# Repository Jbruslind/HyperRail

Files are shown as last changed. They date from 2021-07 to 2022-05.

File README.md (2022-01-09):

<<<<<<< HEAD
# HyperRail

### temporary message- Please view these branches for latest work on HyperRail from Fall 2021 cs467 course.
Currently branches are working with mock data or demo nodes and will be merged to main when it is ideal.

-web_ui (web app development)
https://github.com/Jbruslind/HyperRail/tree/web-ui/WebUI

-ros_sensor_interpretation (self explanatory)
https://github.com/Jbruslind/HyperRail/blob/ros_sensor_interpretation/src/hyper_rail/nodes/README.md

-ros_pathplanning (self explanatory) - https://github.com/Jbruslind/HyperRail/tree/ros_pathplanning
  -merged HyperRail/src from ros_pathplanning to main

-ros_camera_latest (Micasense camera) - https://github.com/Jbruslind/HyperRail/tree/ros_camera_latest

# eGreenhouse 2.0

### Rewrite for cleaner faster eGreenhouse sensor package
=======
# ros_camera_latest Branch

Objective: 
- capture MicaSense images
- transfer image files from SD of Micasense Camera to external storage drive
- store file path of images, along with unique id's to SQLlite database for later retrieval 
- delete files from SD card of MicaSense camera once transfered to external storage drive

Camera details:

[Micasense RedEdge-MX](https://micasense.com/rededge-mx/) 

[HTTP Micasense API](https://micasense.github.io/rededge-api/api/http.html)

Note: Camera API makes request to 192.168.1.83:80 by default

By default, the ethernet IP address is 192.168.1.83 

Please follow [guide](https://support.micasense.com/hc/en-us/articles/215173477-How-do-I-connect-to-MicaSense-sensors-) to connect to camera via ethernet

### Setting up enviromental paths
>>>>>>> ros_camera_latest

The following should be added to your bash.rc or zsh equivalent
```Bash
# Goes above all other source calls
export PYTHONPATH="<Absolute Path>/HyperRail/src/hyper_rail/src"

source <Absolute Path>/HyperRail/devel/setup.bash  
```

<<<<<<< HEAD
If there is a better way to do this please tell me cause this is really annoying

### Basic File Structure Information
---
- src
    - ROS programs, contains all nodes, message types, scripts, and source files. Some ROS functionality is dependent on having the database set up and seeded.
- WebUI
    - Web interface, database, image storage
- ImageProcessing
    - Code created during image stitching research, includes script for generating test images that can be used with the compositor. Compositor depends on having database setup
- stable_firmware
    - stable version and firmware of GRBL to control the appropriate driving hardware

&nbsp;

# ROS Programs
## Description
The HyperRail is controlled by the following nodes and communicate through the message types listed below.
* ProgramNode - Recevies program_ids over `ProgramFeed` topic, gets list of waypoints for the program from the database, coordinates sending movement instructions, data collection instructions, and initiating image stitching.
* MotionNode - Receives individual waypoints from ProgramNode over `MotionService` service, generates GCodes to send to the ESP32 controller. Publishes GCodes to `GCodeFeed` Topic

The following nodes were used during development to test the topics and services. They are available for demonstration, but not used once running with the final hardware.
* ESPMock - Receives over `GCodeFeed`, publishes location to `MachinePosition`
* CameraMock - Receives requests and sends responses through `SensorService`
* SensorMock - Receives requests and sends responses through `SensorService` 

ROS nodes make use of executor classes, db queries, image processing, and constants stored in `~/HyperRail/src/hyper_rail/src`

# Running the ROS programs
In addition to ROS The following libaraies should be installed, either to a virtual environment or globally
* `pip install opencv-python`
* `pip install imutils`
* `pip install argparse`
* `pip install numpy`
* `pip install wheel`
* `pip install pgmagick`

A `Requirements.txt` is included in `~/HyperRail/src` and can be installed with pip

Related topics and services used by the nodes are located in `../srv` and `../msg`

Class definitions used in ProgramNode and MotionNode are located in `../src/communication`

To run the provided nodes, frist run `catkin_make` in the root directory.

The included nodes can be run with the given launch file using one of the following commands:
* `roslaunch hyper_rail hyper_rail_test.launch` - uses mocks for testing message passing.
* `roslaunch hyper_rail hyper_rail_launch.launch` - uses controller nodes to interact with hardware.

Including the argument `--screen` after the launch file name will print the node output to the terminal.

To run the provided nodes and mocks individually for development, run the following in separate terminals:
* `roscore`
* `rosrun hyper_rail ProgramNode`
* `rosrun hyper_rail MotionNode`
* `rosrun hyper_rail ESPMock`
* `rosrun hyper_rail CameraMock`
* `rosrun hyper_rail SensorMock`
* `roslaunch rosbridge_server rosbridge_websocket.launch`

Then send the test program id with `rostopic pub /programs hyper_rail/ProgramFeed "program_id: 1"`

# Image Processing
### File paths
Currently it is assumed that images are stored in the public directory of the web-ui `~/HyperRail/WebUI/public/images`.
Images are stored in using the file structure: `/images/{program_run_id}/{image_type}/{image file}`

Composite images are stored using the file structure: `/images/{program_run_id}/{image_type}_composite{program_run_id}.tif` 

```
public/images/
└── 1
    ├── band_1 
    │   ├── 1.tif
    │   ├── 2.tif
    │   ├── 3.tif
    └── band_1_composite1.tif
```
The image path is set in the settings page of the web-ui and stored in the settings table of the database

### Testing with temporary data
 - Note: the database must be migrated and seeded according to the database setup instrutions for database queries to work.

A test image generation script is included as `/HyperRail/ImageProcessing/drawing.py` This script generates test images which can be used for verifying the compositor crop and layout. To test with this data, generate at least one set of test images in the `~/HyperRail/WebUI/public/images` and run the `create_test_images()` database query, located in `~/HyperRail/src/hyper_rail/src/db_queries.py`. This will assign the set of test images to the waypoint runs for program run 1. 

### Execution
Then the compositor itself can be run on its own using `python compositor.py -p {program_run_id}` or through the program node. In both cases, ensure that `program_run_id` is set to 1 if using these demo instructions.

Until the camera is incorporated into the system, the `ProgramNode` calls compositor.py with a test `program_run_id` which has image paths associated to it. This is assigned at line 119 in program_executor.py and should be removed when the camera is added.

## ToDo:
- Create robust error handling for lost connection with hardware components
- Test with hardware
- Finish sensorAction() function to work with other sensor types.
=======
## Branch Highlights and Setup

### Setup Database and requirements.txt

Install [requirements.txt](https://github.com/Jbruslind/HyperRail/blob/ros_camera_latest/src/requirements.txt) in python enviroment or globally.

In order to test the Micasense Camera, a database is required

Please follow README [here](https://github.com/Jbruslind/HyperRail/tree/ros_camera_latest/WebUI).

Note: make sure schema for database is migrated over

### Test the Micasense Camera with ROS nodes.

Please follow README located [here](https://github.com/Jbruslind/HyperRail/tree/ros_camera_latest/src/hyper_rail/nodes).

Note: CameraMock node is a ros node that controls the camera and it is called via a ros-service named 'camera_service'.

CameraMock is located [here](https://github.com/Jbruslind/HyperRail/blob/ros_camera_latest/src/hyper_rail/nodes/CameraMock). 

### Test MicaSense Camera without ROS nodes.

camera_executor.py can be run [here](https://github.com/Jbruslind/HyperRail/blob/ros_camera_latest/src/hyper_rail/src/communication/camera_executor.py).

Note: the explanation for testing the Micasense Camera will be located at bottom of file below classes.

### Basic File Structure Information
---
- src
    - ROS programs, contains all nodes, message types, scripts, and source files. Some ROS functionality is dependent on having the database set up and seeded.
- WebUI
    - Web interface, database, image storage
- ImageProcessing
    - Code created during image stitching research, includes script for generating test images that can be used with the compositor. Compositor depends on having database setup
- stable_firmware
    - stable version and firmware of GRBL to control the appropriate driving hardware

### Future Plans
Needs to be tested with MicaSense camera connected via ethernet. 

Currently tested with fake data not utilizing Micasense API. 
>>>>>>> ros_camera_latest

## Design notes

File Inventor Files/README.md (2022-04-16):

---
layout: page
title: Mechanical
---

## Overview 

The Mechanical system was designed with modularity and easy assembly in mind. In the future, the system may be deployed in different areas/environment and may require an increase or decrease in dimensions.  In addition, the system will be used by users with little to no prior knowledge of how it was designed or any institutional knowledge of how it was originally assembled. With these aspects in mind, the mechanical system was created with defined "sub-assemblies" in mind so that each sub-assembly is easy to understand and assemble and can integrated into the full system seamlessly. This also allows for the option to upgrade specific sub-assemblies as needed if new ideas or designs are discovered (so long as the base needs are met). 

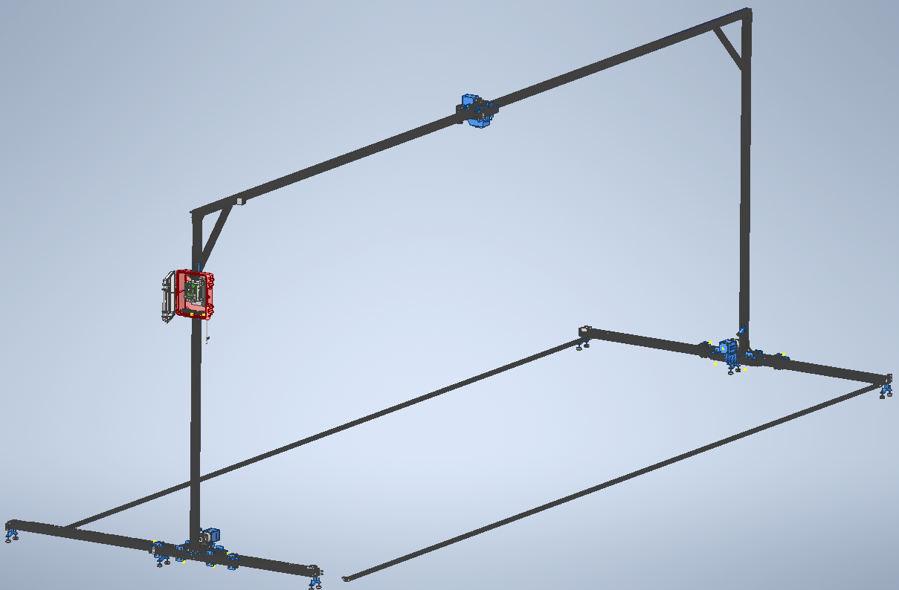
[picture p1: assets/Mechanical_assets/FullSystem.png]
Full System

### Design Objectives 
The main design objectives for this system were: 
1. Modular Sub-Assembly Structure
    * Drop-In Replacements 
    * Iteration 
    * Dynamic Length / Width 
2. Reliable Linear Motion 
    * Long Distance Motion 
    * Self-Contained 
3. Standard Materials
    * Corrosion Resistant 
    * Widely Available 
4. Standard Fasteners
    * Only 1 Allen Key Required for Assembly 
5. Limited Customized Parts
    * Minimize User Manufacturing
## X Carriage Subassembly

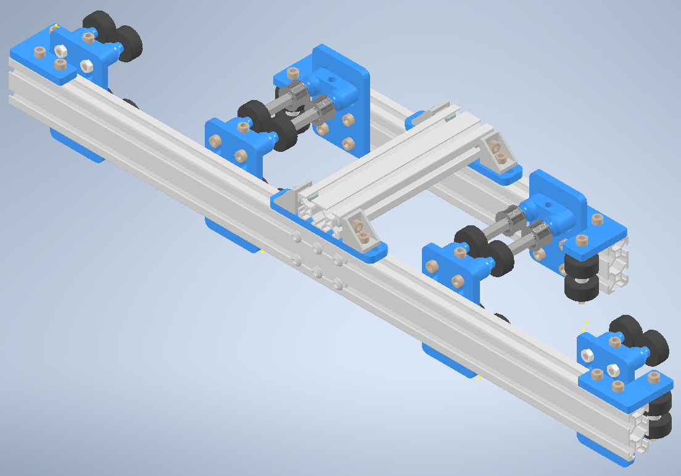
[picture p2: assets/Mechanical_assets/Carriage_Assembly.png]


The X Carriage Subassembly is the main motion platform for the HyperRail system. The assembly should allow for smooth motion along the lower 4060 T-slot track while also allowing the motor mechanism to interface to the belt track. 

The carriage assembly borrows ideas from the [Bell-Everman](https://www.bell-everman.com/products/linear-positioning/servobelt-linear-sbl)[^1] servo setup in which a static belt is used on the tracks and interfaces to a dynamic belt driven by a motor / pulley. A rack and pinion system would also work the same way (with more durability) however the realative costs were prohibitive for a system on this scale. For reference, the average cost per meter for the rack on a rack and pinion is ~$70/m whereas for this style, the belts are only ~$15/m. The projected user needs are for the system to extend up to 90ft or 30m making the rack and pinion very expensive. 

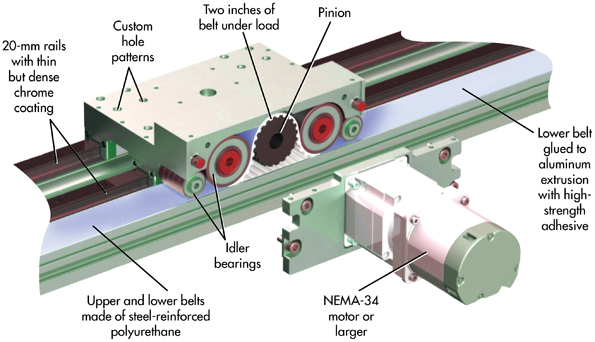
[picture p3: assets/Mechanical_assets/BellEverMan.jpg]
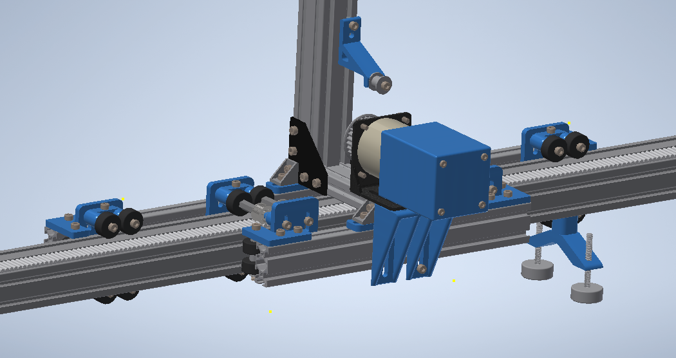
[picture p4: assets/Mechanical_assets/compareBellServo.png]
  

One of the big advantages to this style of mechanism is the ability to easily extend the track length to various sizes without needing to purchase specially made belts/tracks. This allows the overall system to maintain "modularity" with the x-direction, which is aimed to be the longer of the axes (x length >> y, z). If the user wants to add more length, they can easily attach another section of track (4060 with static belt attachment) to the original axis and align the track pieces together so the dynamic belt is able to mesh smoothly (see the Add-On module section). 

The Carriage itself is composed of 3 pieces of 2040 aluninum T slot extrusion which make up the main structural body or chassis. A long piece is used on the side with the vertical beam to give it added support and a smaller piece is used on the side with the motor. 

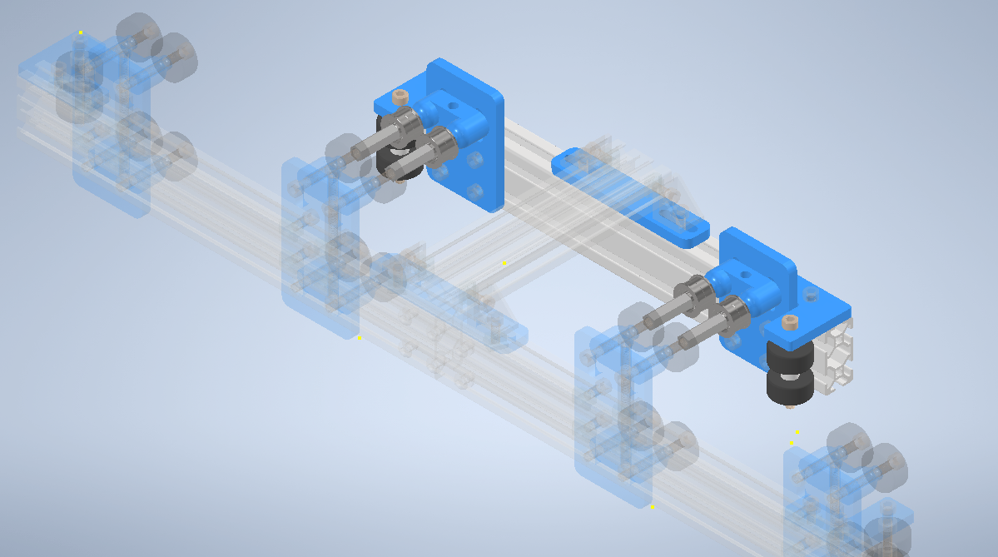
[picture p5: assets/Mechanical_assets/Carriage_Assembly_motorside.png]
Smaller Side


Individual plates with delrin wheels are used for rotational motion and structural stability. 

## X Rail Assembly

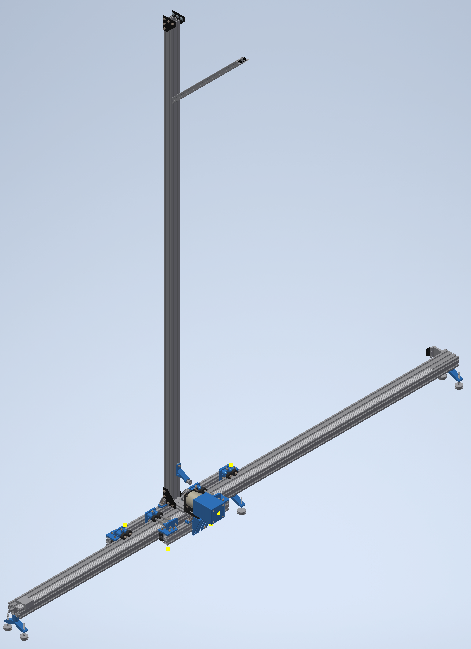
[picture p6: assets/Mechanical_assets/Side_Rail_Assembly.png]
X Rail
 Side Profile X Rail

The X Rail Assembly utilizes the carriage shown above combined with a track and vertical 4040 T-slot beam. The track itself is made of 4060 aluminum which was chosen for symmetry and stability (increased mass provides a good counterweight). In order for the mechanism to be stable, the carriage base needs to equally distribute mass where the most mass comes from the vertical beam + upper axis and the motor + planetary gearbox. Therefore the X Rail Assembly cantilevers the 2 largest masses against each other so the center of gravity is relatively centered within the X carriage.

The assembly is supported by a foot subassembly which can be added and distributed as necessary to support the system in different environments. 

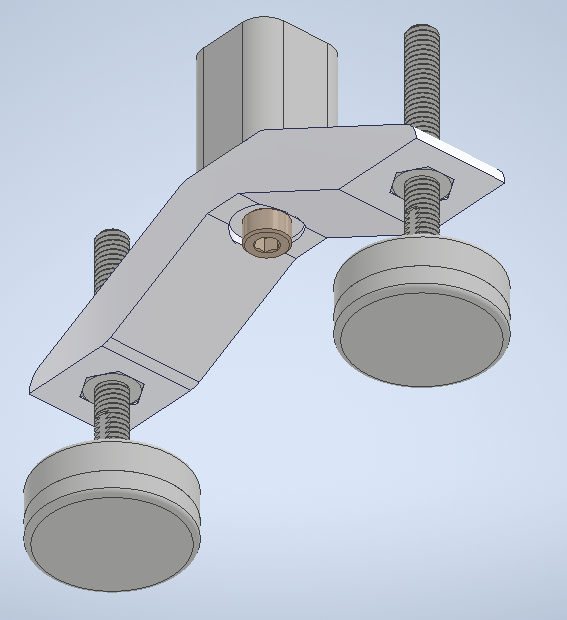
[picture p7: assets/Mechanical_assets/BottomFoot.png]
Bottom Foot


These feet allow for small height adjustments on either side through an M6 bolt embedded in the design which can be useful for outdoor use on rocky / dirt environments.

The pulley attached to the motor can be adjusted using the right angle brackets and can be used to provide tension to the belt system (height adjustment shown below). The whole mechanism can then be moved using the dynamic belt rolling along the static belt 
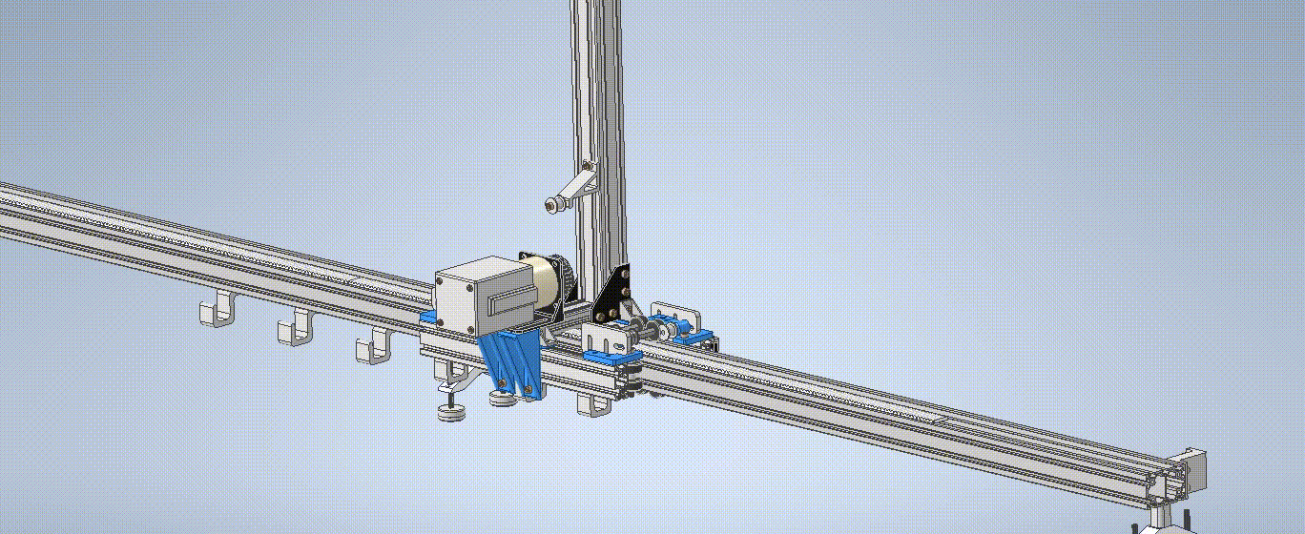
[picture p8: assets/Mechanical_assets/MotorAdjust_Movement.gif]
X Rail Movement


The static belt layer is comprised of HTD 5mm, 25mm width polyurethane belt with steel cord reinforcement from [PolyBelt](https://shop.polybelt.com/20-5M-Open-End-Belt-Roll-Polyurethane-with-Steel-Cords-B20-5M-MPS.htm). Polyurethane was chosen for its durability and resistances to outdoor environments and steel cord was chosen for its price point. Kevlar reinforcement was another option which had a better tensile modulus (lower stretching over time) however this was determined to not be a huge factor since the static belt wouldn't have large segments stretching at the same time (the stress is localized to each individual point). At the same time, Kevlar has larger thermal fluctuations [^2] which could cause problems during outdoor use in freezing / hot temperatures.

This profile is standard across many suppliers but PolyBelt was chosen for their price point and US location. In addition they had a matching closed belt profile which was the right size (6mm) and length (635mm) for the dynamic belt system.

## Top Frame Subassembly

The top frame subassembly was meant to serve as the Y-axis for the overall system and is comprised of a main 4040 T-slot extrusion paired with the same Bell-Everman style linear motion as the X-Carriages. 

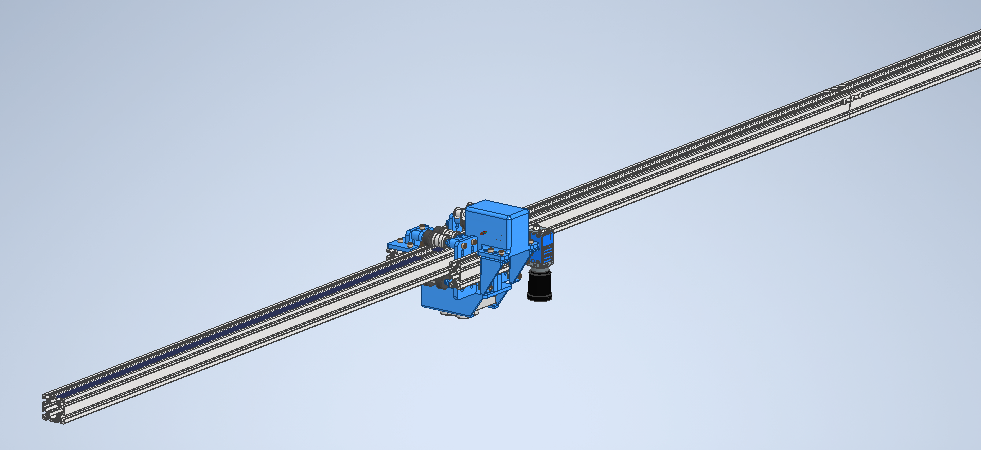
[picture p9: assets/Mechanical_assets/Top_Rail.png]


The hollow channel within the T-slot extrusion serves as a pathway for wiring from one side of the system to the other, specifically for the motor and magnetic endstop wiring. These wires are static with respect to the gantry and so can be threaded through without any torsion later. 

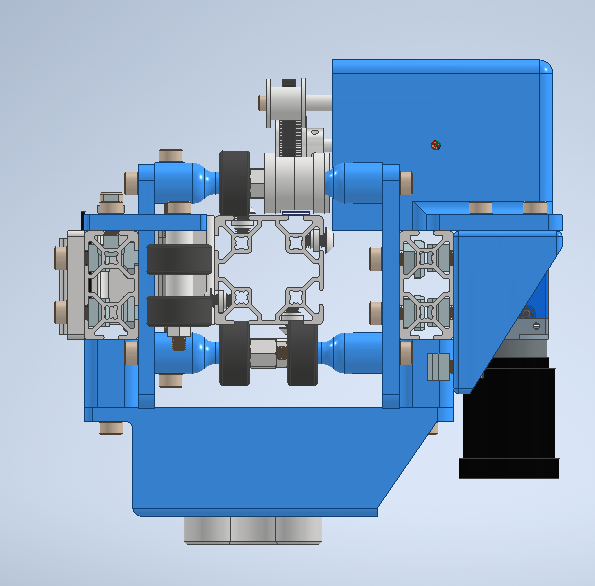
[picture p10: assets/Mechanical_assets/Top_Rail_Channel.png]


## Y Carriage Subassembly

## Ebox Subassembly

## Main System

## References
[^1]: Bell-Everman, Inc. (2016, October 19). New ServoBelt™ LoopTrack Linear Stage. Retrieved from https://www.bell-everman.com/products/linear-positioning/servobelt-linear-sbl
[^2]: When to consider Kevlar reinforced belts for linear motion applications. (2019, July 05). Retrieved from https://www.linearmotiontips.com/when-to-consider-kevlar-reinforced-belts-for-linear-motion-applications

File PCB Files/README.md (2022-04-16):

---
layout: page
title: Electrical
---

## Overview 
The electrical subsystem was designed with 3 key elements in mind: 

* Plug and Play operation 
* System Reliability 
* Expandable operation 

Plug-and-Play operation was taken to mean minimal requirements for hookups and other connections and to prioritize standard connectors that are easily available from commercial outlets. System Reliability was necessary for operation under a wide variety of conditions (wide Vin range, built-in protections, and temperature/humidity resistance) and to limit repairs by the user. Finally, it was assumed that this system should be able to accommodate other configurations than just a 3D CNC gantry and should have features that can be expanded for later development. 

## System Diagram 

System Diagram

A system diagram was created to help design the infrastructure and architecture for the overall system. In this case my idea was to approach every operable component as a "node" which could act as an independent unit. The reasoning being that I could assign each "node" to team members and give them a black box explanation for each. As an example, the motor node circuit needed to operate using the following parameters: 

+----------------------+-----------------------------------+
| Parameter            | Valid ranges                      |
+======================+===================================+
| Vin Range            | 12 - 30V                          |
+----------------------+-----------------------------------+
| Motor Current (rms)  |  2A                               |
+----------------------+-----------------------------------+
| Signal Inputs        | Step, En, Dir (STEP/DIR control)  |
+----------------------+-----------------------------------+
| Step Frequency       | < = 5Khz                          |
+----------------------+-----------------------------------+
| Microstepping        | 1x - 16x                          |
+----------------------+-----------------------------------+
| Input Interface      | RJ45 8 pin                        |
+----------------------+-----------------------------------+

By providing the specification and known inputs / outputs I could keep each node organized and have the ability to assign its development to any members that were working under my at the time. 

The main blocks in the system diagram that needed to be developed were: 
* Integrated Stepper Driver (Motor Node) 
    * Motor controller using DIR/STEP controls (or eventually UART)
* ESP32 GRBL Controller 
    * This node was meant to be the main firmware controller which would determine the signals to be sent to each motor to tell it where to move. This could be abstracted to basically just run any CNC control firmware such as Marlin, GRBL, or LinuxCNC. While researching it was determined that the ESP32 GRBL firmware met all the requirements and more with little to no development necessary (see the ESP32 GRBL section)

## Motor Nodes

Motor Node

The Motor Node PCB was meant to be an independent solution for stepper motor control. The idea was there could be many motor "nodes" which could be controlled using a known standard protocol. The controlling board could be adaptable to a variety of stepper motor types and would be easily mounted to the motor itself. 

Motor node mounted

The node has 3 I/O connectors for different purposes. The RJ45 connector (commonly used as an Ethernet connector) is used for Power and Control to the Stepper Driver IC: 

Ethernet Highlight

The pinout diagram can be found on the schematic pdfs which are included within the documentation under "HyperRail\PCB Files\Integrated Stepper Motor Driver-(fab,pcba)\PCBA-Integrated Stepper Motor Driver"

### Stepper IC 

Pinout Schematic

* Red (bottom right) | RJ-45 Pinout   
    * This Pinout is used for Power input and control signals to the TMC2209 driver IC 
* Pink (Top) | Sense Resistors 
    * The sense resistor selection is incredibly important to the TMC driver current limits. If a larger / smaller motor is required, then these should be changed to reflect that using the recommended lookup table (taken from TMC2209 Datasheet, section 8): 
    
* Yellow | VRef Selection 
    * The VRef circuit uses a simple voltage divider to maintain "soft" current limits. The idea is that the sense resistors set the "hard" current limits in that they are hardware defined whereas the voltage divider circuit allows the user to customize "soft" limits. A radial potentiometer is used for adjustable resistance and a silkscreen diagram is provided to indicate the direction to turn to increase motor current. 
* Blue | Motor Phase Outputs 
    * The output for the motor phase currents from the Stepper Driver IC is a simple 4 pin screw terminal. This allows users to use a variety of stepper motors without having to find / assemble special connectors. All that's necessary is to determine the phase diagram, strip the wires and plug in. 
    


### Power Conversion and Status LEDs



* Red | Buck Converter 
    * Main buck operating circuit which are simply an input and output capacitor and the integrated module. 
* Blue | Reverse-Protection Diode 
    * Prevents negative spikes or reverse current 

Power Conversion is done using an integrated buck controller / switch, the TI  [LMZM23601V5SILR](https://www.ti.com/product/LMZM23601). This is a wide Vin range (4 -> 36V) buck converter which will step down the power input (expected 12 - 24V) to logic level (5V) for the Stepper Driver. Not much current is expected for this application, the estimated current draw by the driver for logic level is 10mA max: 





There are 2 physical test points which were designed for multimeter probes to easily measure the voltage output during manufacture and testing. 
## ESP-32 Controller

The ESP-32 Controller was designed to be the liaison between motion requests by the ROS software and the rest of the machine. The board itself is computationally powered with an ESP32-WROOM module (either through a daughter dev-board or embedded on the board) running the [GRBL_ESP32](https://github.com/bdring/Grbl_Esp32) firmware. A key aspect of using the GRBL style firmware over other flavors (such as Marlin or otherwise) is that GRBL supports the ESP32 with no perquisites and can support a Web-UI natively for manual control. 

GRBL Controller

## Magnetic End Stops

## Main System

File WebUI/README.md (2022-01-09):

# HyperRail Web Interface

## Ruby Version

This project is a [Ruby on Rails](https://rubyonrails.org) application configured to use [Ruby](https://ruby-doc.org) version 2.7.4, but that is not a hard requirement.
Changing ruby versions will require a new Gemfile and modification to `.ruby-version`.

## Configuration

Once version 2.7.4 is installed, the rest of the gems can be installed using `bundle install`.

## Database Setup

The [SQLite](https://www.sqlite.org/index.html) database can be initialized using `bundle exec rake db:create`.
The database can be initialized using `bundle exec rake db:migrate`.
Some test data can be populated in the database by typing `bundle exec rake db:seed`.
At any point, the database can be recreated and repopulated with seed data by typing `bundle exec rake db:reset`.

The default password is `default-password` but it can be changed by creating a `Setting` in the console, or by changing the password in the `Settings` tab.
To access the console, first type `bin/rails c` and then update a `Setting` using the following example:

```ruby
# Find the existing setting or create a new one if it has not yet been created
setting = Setting.find_or_initialize_by(name: 'password')
setting.value = 'new-password-here'
setting.save!
```

## Running

To run the web server, type `bin/rails s`. By default it will run on port 3000 and can be reached at http://localhost:3000/.
Sessions are handled by storing an encrypted, signed key with the last password used and login time, and do not currently time out.
If the password setting changes, a re-login will be required as it is checked on every request.

## Default Program

Though multiple programs can be saved and run, the analysis interface assumes that there is currently a single program running that will cover the entire greenhouse. If the greenhouse settings change in terms of camera height, field of view, length, or width, a new default program will need to be generated. To do so, start the console using `bin/rails c` and run the following command (changing the name if desired):

```ruby
Program.create_from_settings(name: 'Default Program')
```

Once this has been done, you can delete the old program using the web interface.

## Default Program Generation

The default program is generated by covering the calculated greenhouse area with waypoints in a grid pattern, and then covering them using back-and-forth paths.
The grid size is calculated by using the height of the camera, its field of view, and incorporating an amount of image cropping to account for parallax due to subject proximity.
This is currently ballparked at 25% but will require experimentation with the real camera and plants in order to know if this is correct.
It is expected that this program generation will require some slight modifications once it is applied to the real hardware.

## Mock Seed Data

The `bundle exec rake db:seed` command executed above will fill in some fake sensor readings and anslyses.
A good way to get started with a new installation is to configure the default settings in `db/seeds.rb` to match the physical greenhouse and camera, and have that backfill some mock data.

## To Do

* Integrate [`rosbridge`](http://wiki.ros.org/rosbridge_suite) into a startup script so that it starts with the Rails application
* Export images once they are taken and stitched with camera ros nodes
* Add default program generation to the UI to remove a console interaction
* Map an analysis to a specific program in case the dimensions change to prevent loss of historical data
* Integrate GCode sending from relevant rosnode branch on dashboard
* Add ability to launch program manually from `Program` tab
* Dynamically scale SVG element to container panel
* Account for non-square camera images during program generation

## Development Notes:

Below are some helpful links to consider when modifying the interactive grid.

SVG Basics - https://developer.mozilla.org/en-US/docs/Web/SVG

How to properly scale svg elements - https://stackoverflow.com/questions/19484707/how-can-i-make-an-svg-scale-with-its-parent-container

SVG viewport and viewbox concepts - https://webdesign.tutsplus.com/tutorials/svg-viewport-and-viewbox-for-beginners--cms-30844

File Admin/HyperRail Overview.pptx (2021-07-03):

## hYPERrAIL pROJECT Overview

Jorian Bruslind

## Little bit about me

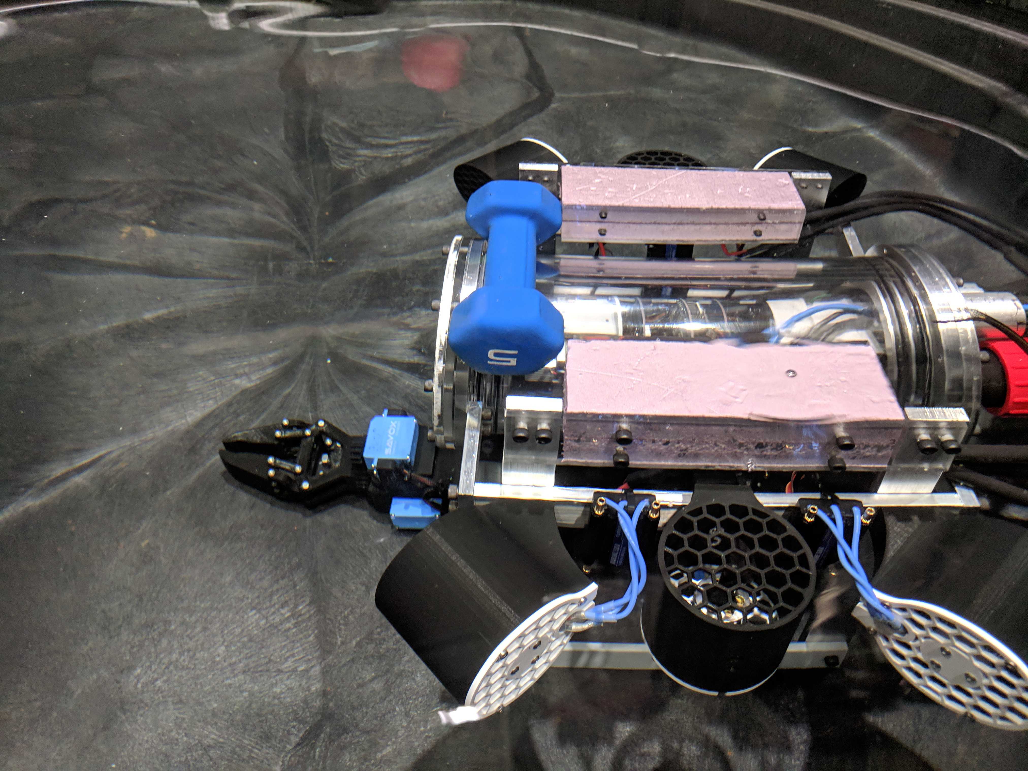
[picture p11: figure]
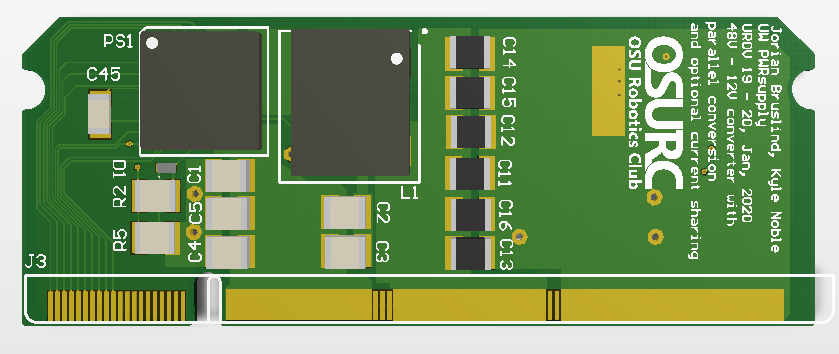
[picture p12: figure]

- Senior in ECE (Graduating at the end of Winter)
- Part of the OSU Robotics Club (2016 – 2020)
  - President (2017-2019)
  - Underwater ROV Team lead (2016-2020)
- Enjoy doing electronic projects in my spare time
  - Home automation
  - Server management / IOT networks
- Capstone Project focused on Robotics / Automated systems
  - Automated Microbial Analysis

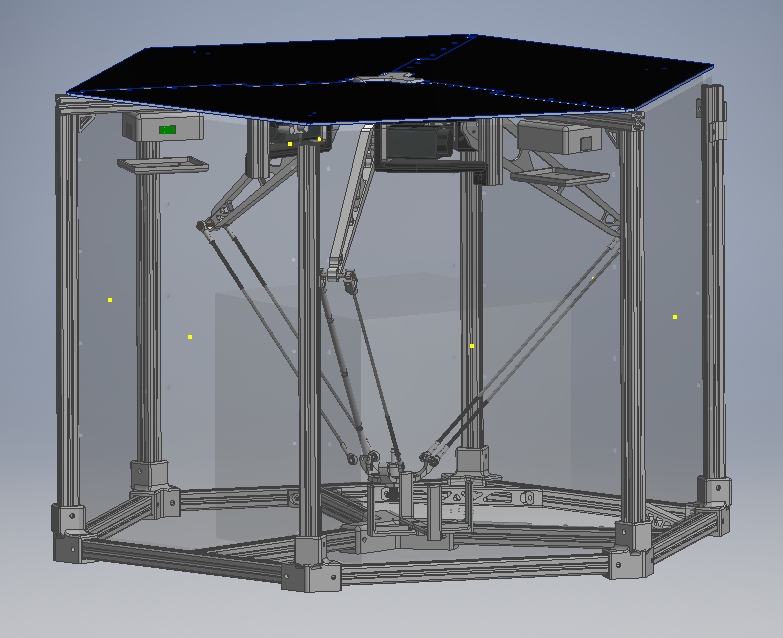
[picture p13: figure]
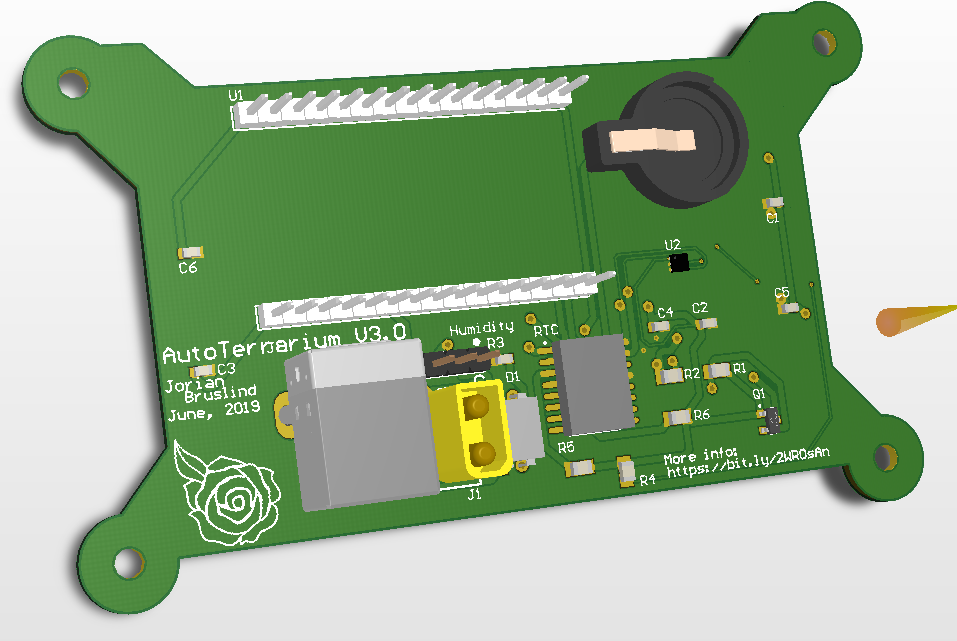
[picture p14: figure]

## Master’s program

- 45 Credit program, Project based
- Faculty advisors will serve to grade project scope and assist in planning
- Current timeline:
  - Spring 2021: 2 Project Credits (ECE 506)
  - Fall 2021: 2 Project Credits
  - Winter 2022: 4 Project Credits
  - Spring 2022: 4 Project Credits

## Current State

- Gantry like system to move an end effector in 3D space
- Axes are pretty locked up and the carriage needs some fine tuning
- Custom firmware built for stepper motor control
- Processing GUI used in conjunction with Adafruit M0 Feather
- Some LoRa capabilities

## Junior Design Groups

- 4 dedicated groups to working on the HyperRail System
- Each group is responsible for motion control using the current system (4x stepper motors + microcontroller)
- Each group has been tasked with a unique requirement to improve on the system
  - Joystick control from computer
  - Power feedback with low power algorithm
  - Path planning from image
  - Wifi control through web interface

## My work so far

- Created new 3D model using Inventor
  - Rebuilt frame and linear motion carriages using current components (with some new 3D printed components)
- Researched implementations of gantry system in similar use-cases (also some parallel cable robots)
- Created discord server for Junior Design groups and am currently helping them figure out implementations / debug
- Working with STEMbassadors for support in manufacturing / design

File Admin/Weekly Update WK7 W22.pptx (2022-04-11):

## Weekly Update

Jorian Bruslind
Week 7

## HyperRail Project

- Current Status
  - Integrated new RGB camera into system
    - Some challenges with lighting and streaming
    - Easy to use with correct software installed
  - Updated Web interface to give access to images
    - Can download latest runs as .zip files
    - Having trouble with preview function (no idea how ruby works)
  - Scheduling conflicts with defense meeting

## Current Status

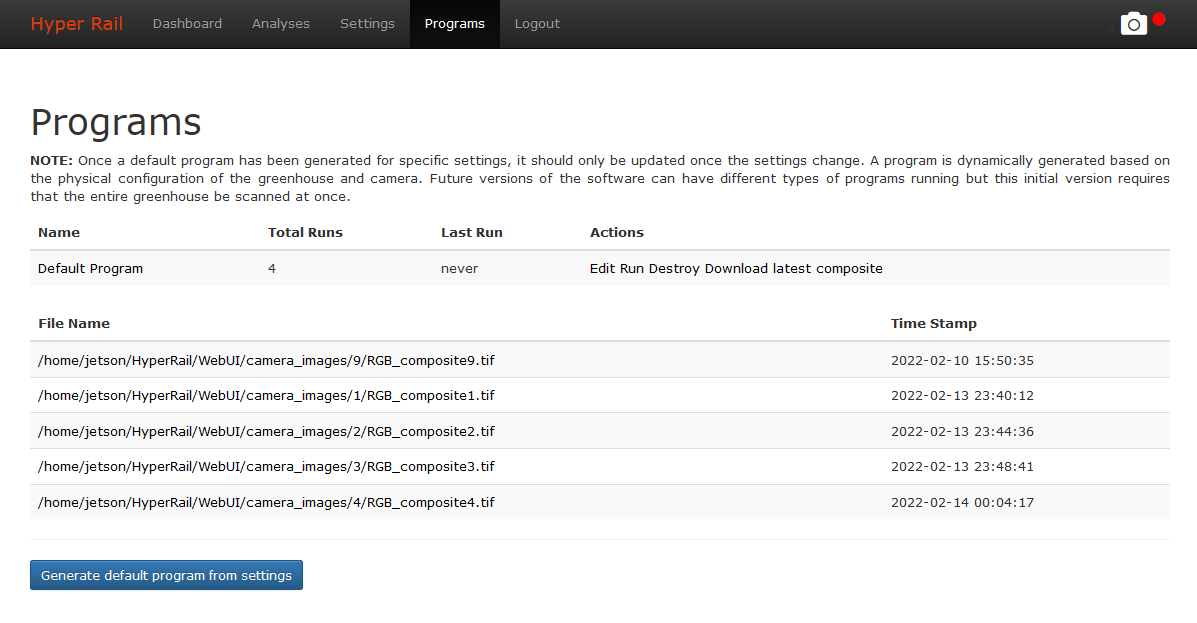
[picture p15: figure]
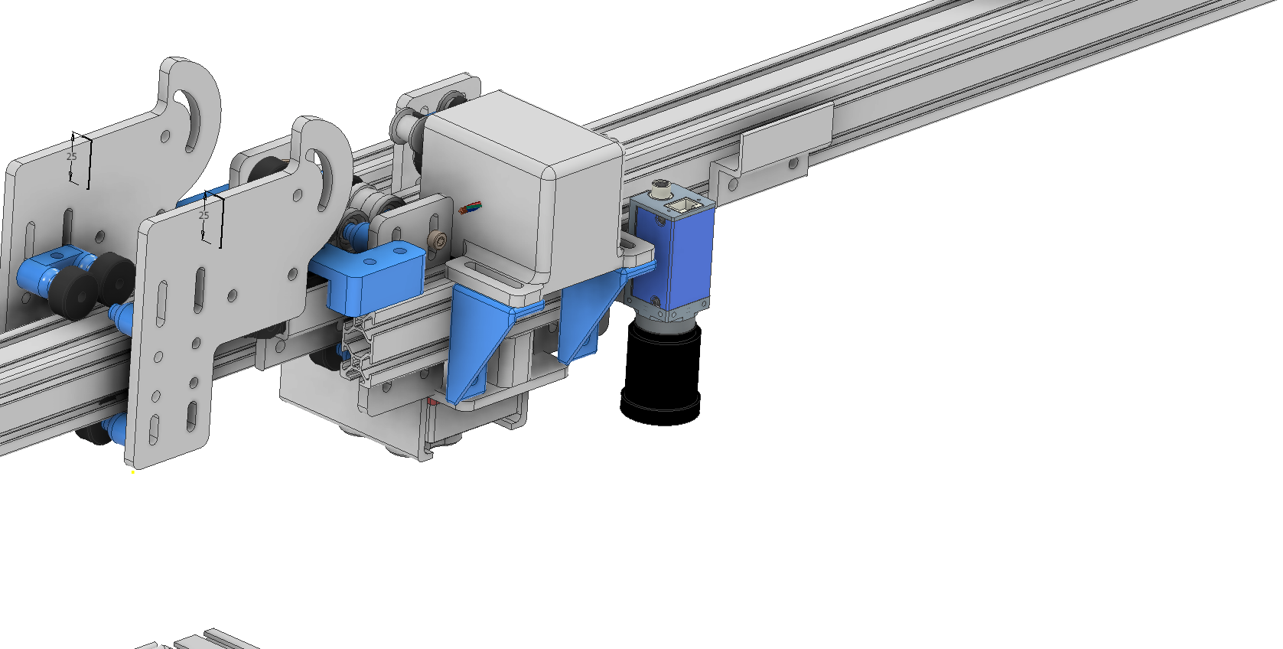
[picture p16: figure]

## Project Work

    - Working with both IE and ME capstone teams to develop hardware further
    - ME team is working on stability and assembly components
      - Better carriages (CNC aluminum vs 3D printed plastic)
      - Better wire guides (current guides are limited by length)
        - Festoons! <- One of the best ideas
      - Better structural stability
        - Employ tensioned cable as gusset supports
    - IE team working on documentation and assembly designs
      - Exploding 3D models into Lego-like designs
      - Writing and drafting instructions
      - User feedback for current system design (from user perspective)

## Next Steps

- Installation date confirmed for March 1st (Tuesday)
- Need to create skeleton for defense presentation for review (preferably by this week)
- Tear-down of system for ME/IE team and to retrofit for smaller footprint

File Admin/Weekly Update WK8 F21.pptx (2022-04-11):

## Weekly Update

Jorian Bruslind
Week 9

## HyperRail Project

- Current Status
  - Updated Y-axis now moves freely over the upper 8020 beam
    - Problems with the belt continuity (slipping over static belt)
    - Tensioning needs to be tuned to determine optimal stress
    - 3D printed shroud for motor node + stepper mode
  - Oscillations in the gantry due to lack of surface area contact
    - Looking to increase carriage length and add additional supports
    - Researching Tuned Mass Dampers to minmize vibration on the upper carriage

## Current Status

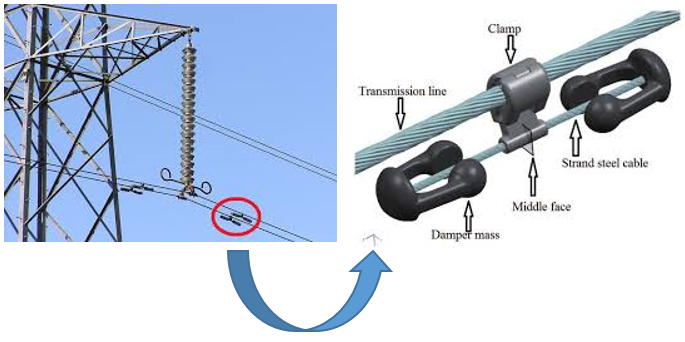
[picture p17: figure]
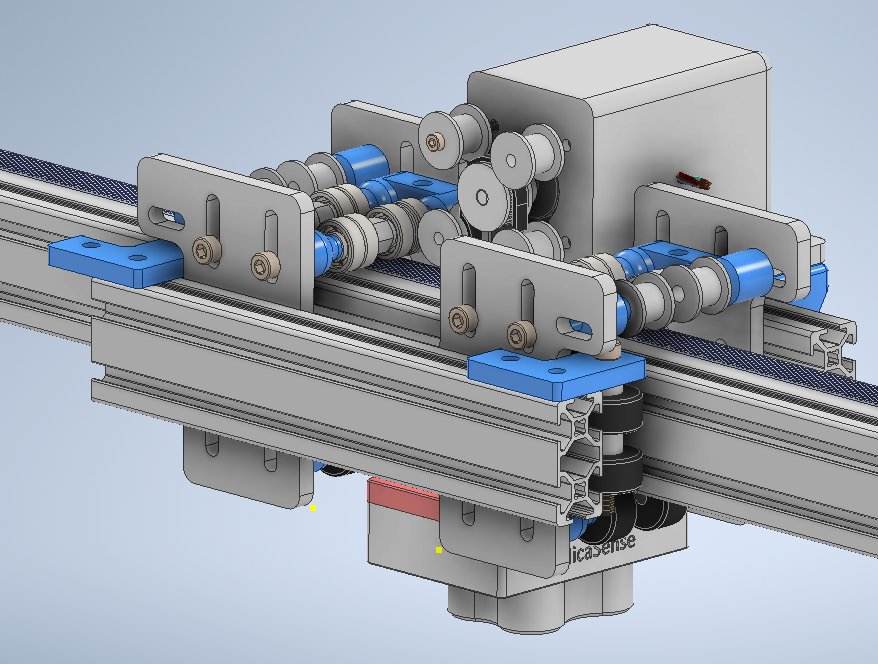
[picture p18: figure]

## Project Work

  - Meeting with CS capstone team regularly about requirements and work
    - Have a rough draft for the user interface and a wire diagram showing connections
    - User will be able to define “image area” and the program will determine images
  - Looking for finalized components for upper belt
    - Thickness and tension becoming an issue
  - Homing sequence and encoder needs to be implemented
    - Finally have prototype with motion, can implement homing

## Next Steps

- Register for classes next term (ECE 576 vs ECE 599 (CPS)
- Test homing feature along with motion repeatability
- Add wiring harnesses into frame
- Finish testing speed with automated tests
- Order finalized components (made from CNC aluminum, not PLA/PETG)

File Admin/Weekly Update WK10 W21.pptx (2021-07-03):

## Weekly Update

Jorian Bruslind
Week 10

## HyperRail Project

- Current Status
  - Helping Junior Design students assemble systems
    - 3D printing components
    - Tools / Workstations on campus
    - Online debugging or in person
    - Wire purchasing / connector suggestions
  - Most mechanical work done, ready for students to test

## Current Status

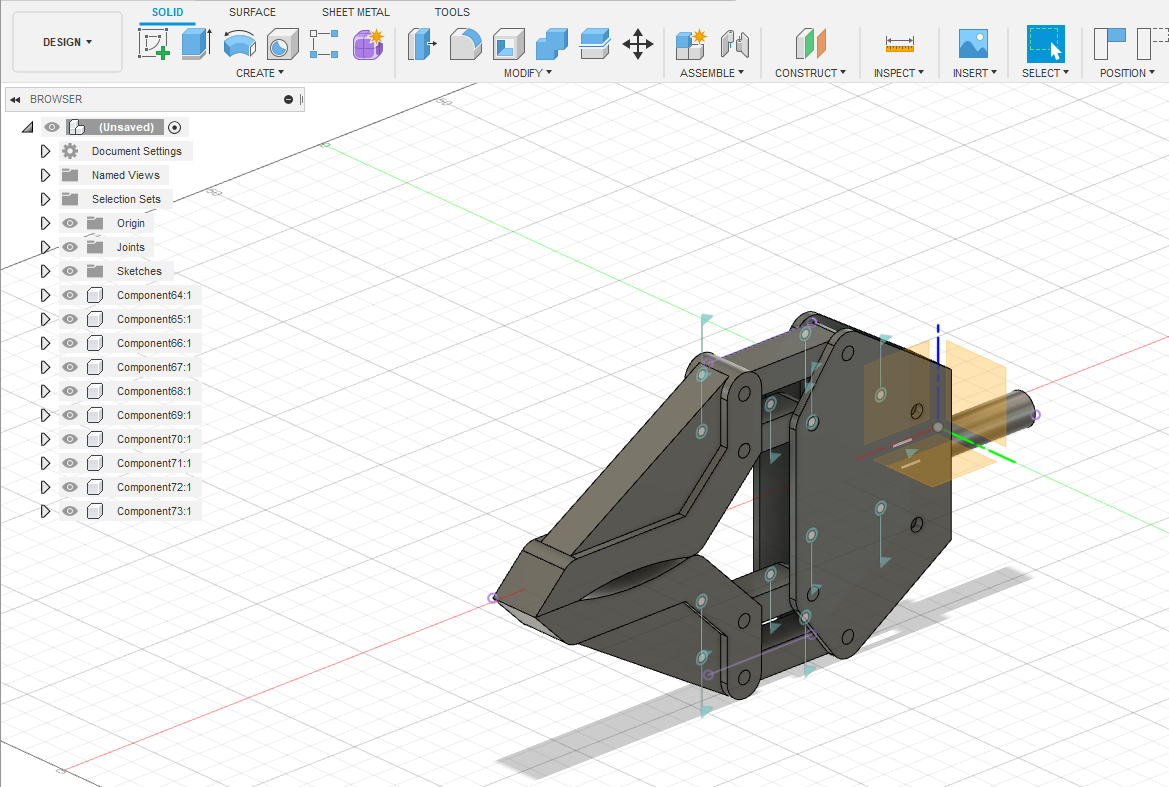
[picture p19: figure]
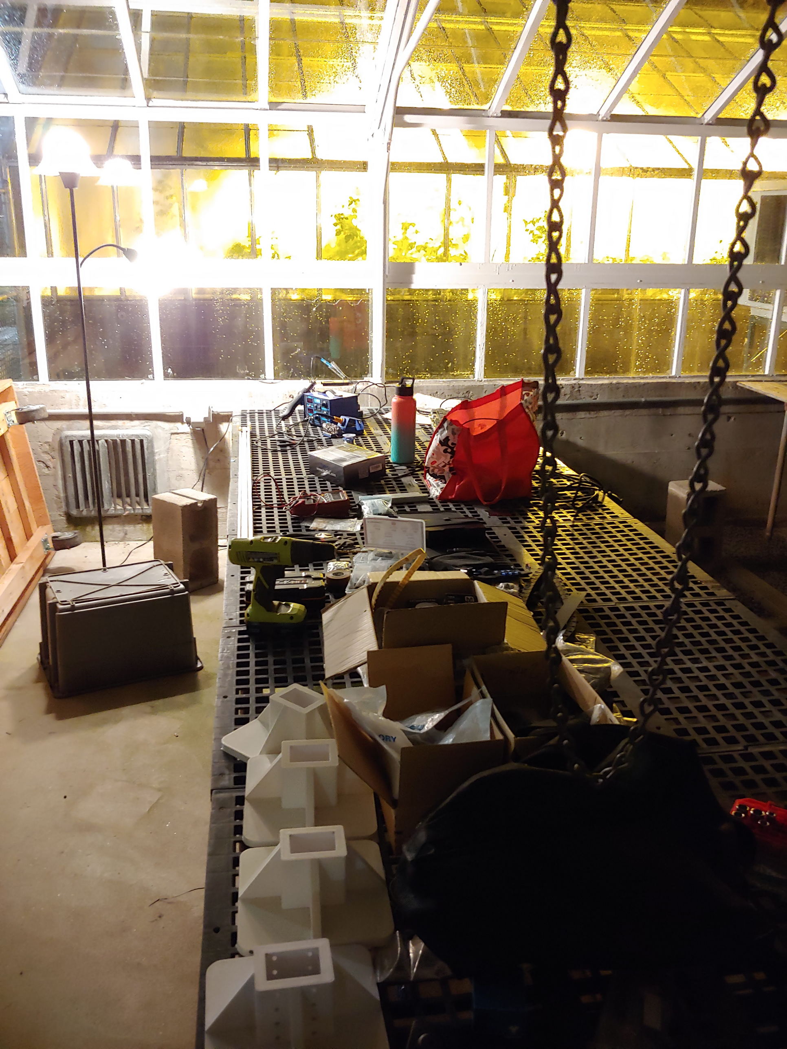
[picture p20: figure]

## Project Work

- Junior Design System Verification
  - Meeting with teams all this week to assemble / test
  - Verification for all groups by the end of this week
- Looking into integrated stepper drivers
  - Mechaduino
  - TMC2209 – TMC2225
  - Magnetic Feedback encoder

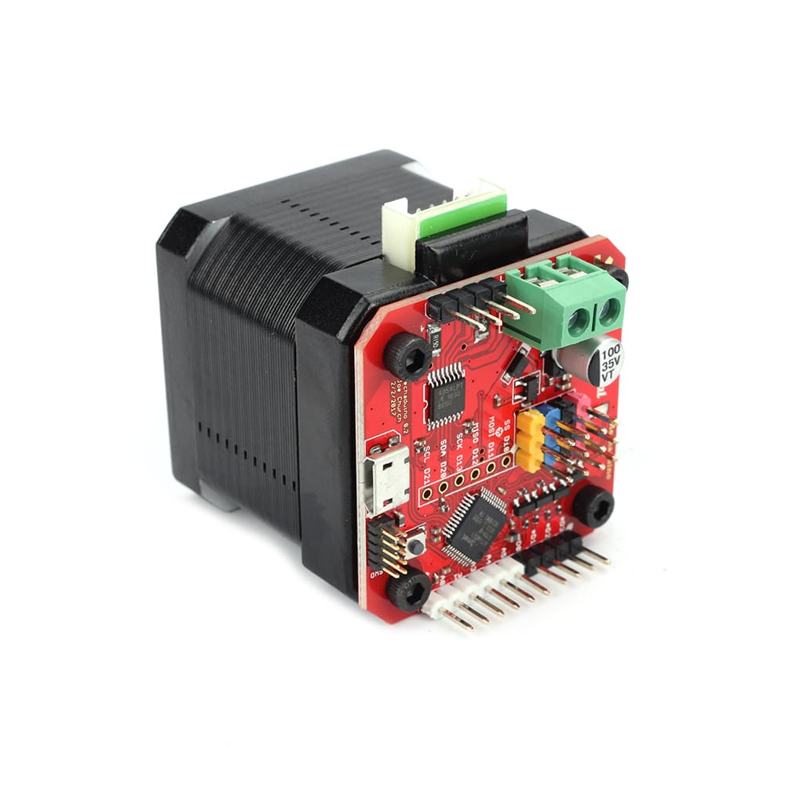
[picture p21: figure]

## Other Work

- Finite Difference Time Domain Method in Adv Electromagnetics
  - Everything can be boiled down to estimating very small parts of a response and adding them all together
  - Final few projects

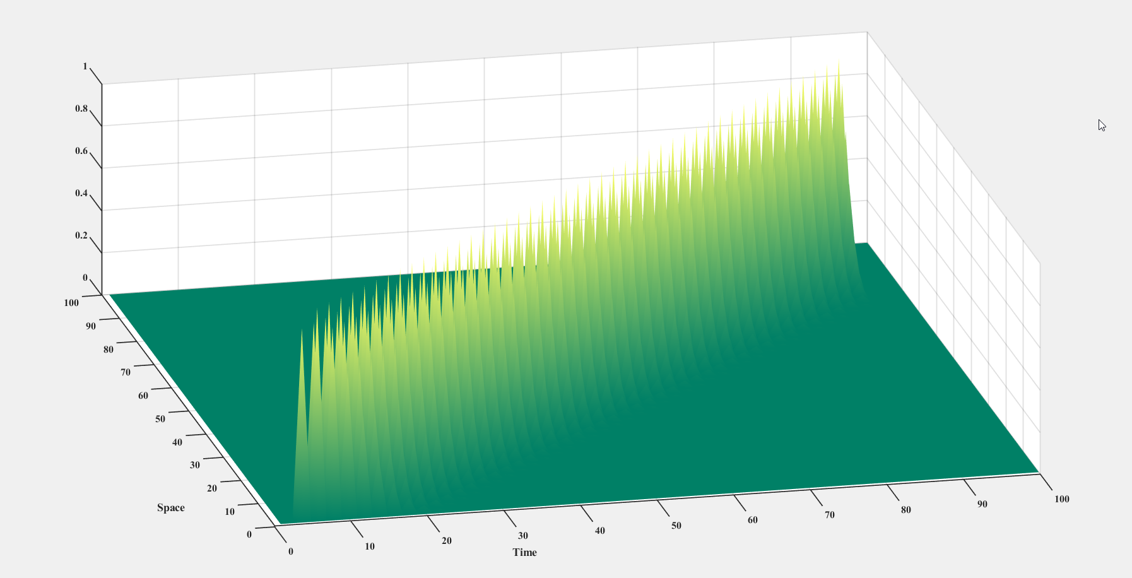
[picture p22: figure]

## My Plan

- Keep up with projects and school work
- Start testing full system with Junior Design team
- Integrate ESP32 GRBL with control system for next term

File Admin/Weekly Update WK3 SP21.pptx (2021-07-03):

## Weekly Update

Jorian Bruslind
Week 3

## HyperRail Project

- Current Status
  - Working with project stakeholders to integrate into site
    - NWREC (North Willamette Research and Extension Center)
    - On-campus greenhouses
  - Making improvements to controlling circuits
    - New integrated drivers
    - Better main controlling board
  - Slight improvements to mounting hardware
    - PETG upgrades for rain / UV resistance

## Current Status

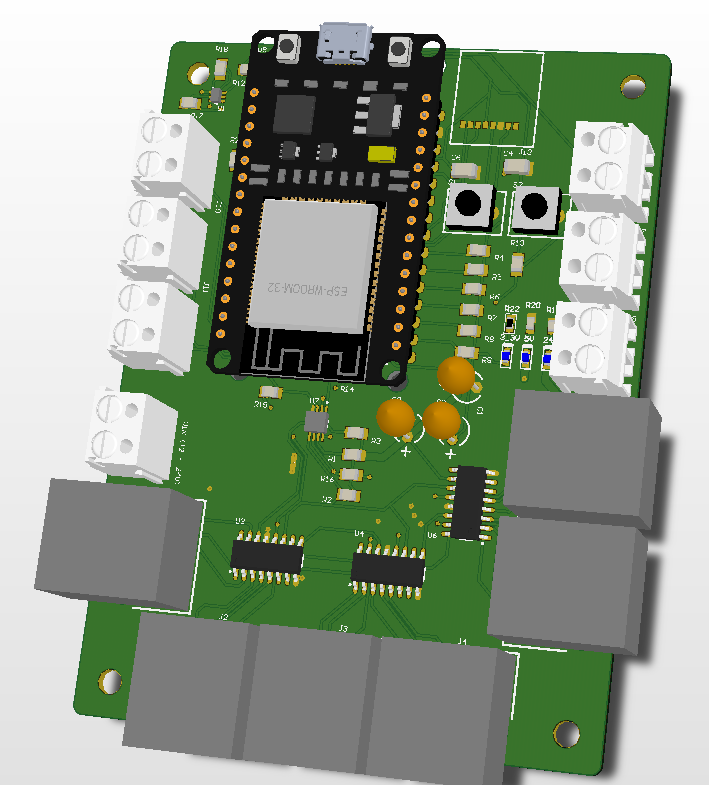
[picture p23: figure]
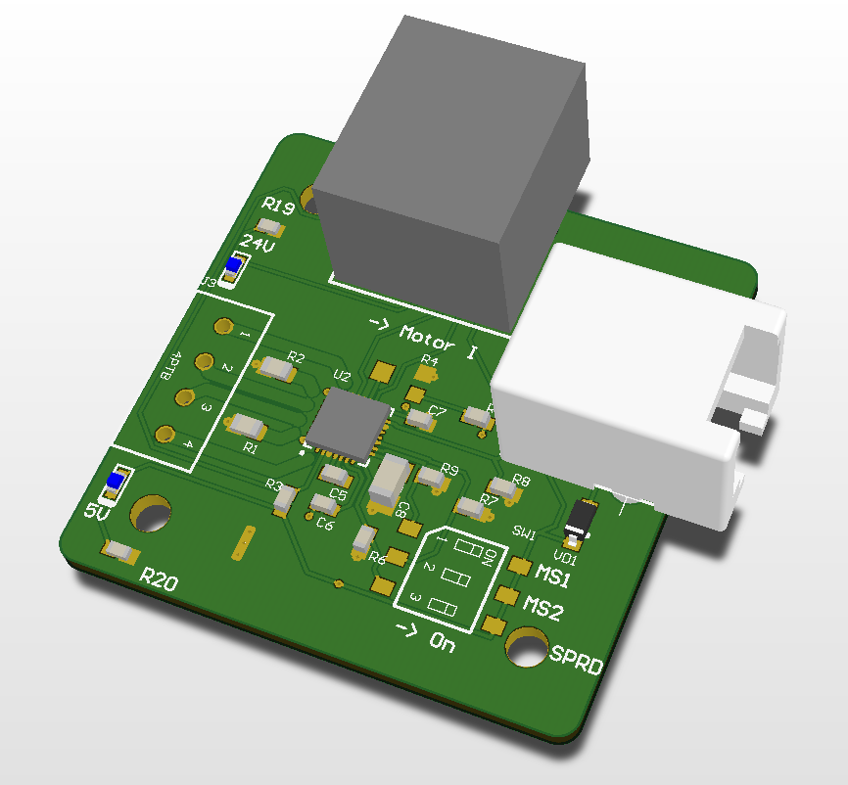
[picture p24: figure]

## Project Work

- Integrated Stepper Driver
  - TMC2209 breakout board for stepper motor controller
    - Modular connection points (POE+)
    - On-board voltage conversion
    - Customizable (current and driver mode)
- ESP 32 GRBL
  - Built-in wifi control
  - Serial communication through USB with Gcode
  - Optional SD expansion
  - Up to 6 axis control (independent)


## My Plan

- Order enough components for full prototype
- Assemble 4x stepper drivers, 1x ESP32 GRBL
- Test design and check for any problems
  - Coordinated control
  - Automated control over USB / Wifi
  - Torque limit tests
- Submit program of study

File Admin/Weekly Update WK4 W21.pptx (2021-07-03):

## Sales pitch

Subtitle goes

## Hyperrail Project

- Project goals:
  - Create a modular, inexpensive method to analyze crops using hyperspectral imaging
  - Have an easy to use interface for general use (greenhouse technicians, RA’s, etc)
  - Document project details for future iterations
- Current project iteration is to use a gantry
  - Project implemented 2 axes with plans in place for a 3rd
  - Custom firmware written for Adafruit Feather M0 with stepper drivers
  - UI implemented in Processing
- Project support from the OPeNs Lab (Openly Published Environmental Sensing)

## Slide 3

- System as-is


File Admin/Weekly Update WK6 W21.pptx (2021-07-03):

## Weekly Update

Jorian Bruslind
Week 6

## HyperRail Project

- Project Goals
  - Create a modular, inexpensive system to take hyperspectral images of crops
  - Develop a user friendly interface to for use by technicians, RA’s, etc
  - Create good documentation for later iteration
- Current Status
  - Developed new system frame for better tension and carriage motion
  - 3D printing new parts for verification, looking to purchase COTS products later
  - Working with Junior Design teams on standardization
  - Trying my best to do testing while in quarantine

## Current Status


## Project Work

- Junior Design Block 1 Checkoff
  - Met with Junior Design teams for the Checkoff
  - Teams seem to be on track and good development so far
  - Having teams look into using GRBL and Marlin for interpreters
    - ESP32 implementation for GRBL is awesome
- Met with project stakeholders
  - Established preliminary scope (size, rough cost, deliverables)
  - Goal is to create at least working module with current parts
- Met with STEMbassadors
  - Student Club on campus dedicated to innovation and CNC machines
  - Very excited about HyperRail Project

## Other Work

- Midterms
- Nvidia Internship :D

## My Plan

- Create complete block diagram with project timeline
- Look into SpyderBot for different implementation
- Get a rough order of magnitude (ROM) for system costs
- Create system artifacts
  - System Interconnect Diagram (SID)
  - Bill of Materials
  - Software flowchart / state machine

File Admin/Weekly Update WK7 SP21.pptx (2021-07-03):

## Weekly Update

Jorian Bruslind
Week 7

## HyperRail Project

- Current Status
  - Trying to get some workdays together to test the new upgrades
    - Bell-Everman servo belt test
    - PETG 3D prints
    - Better delrin wheel mounts
    - Actual PCB drivers
    - Wifi Control

## Current Status


## Project Work

  - Not much else going on, need to test everything before improving
  - Working on creating a web site GUI for controls (HTML / ROS based)
    - ROS JS calls through HTML JS, most likely running on some RPI or SBC
    - First iteration will have some basic controls and system feedback (states, location, etc)
  - Integrate Magnetic Limit Switches into design
    - Just need some mounting platforms and wiring
  - Other wiring parts need to be planned for
    - ESTOP
    - Joystick control
    - Fuses / Protection


## My Plan

- Do a quick test of the GRBL system with all the new changes, check for issues and improvements
- Design and purchase a main housing for electronics w/ ESTOP and auxiliary control
- Extensive stress tests with motors to make sure nothing will go completely wrong in the field (random failures, mechanical errors).

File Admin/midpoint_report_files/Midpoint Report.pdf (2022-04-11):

CS 467 - Fall 2021

Greenhouse HyperRail Research: Midpoint Report

Project Owner/Mentors
Jorian Bruslind
Chet Udell

Team Members
Kelley Reynolds, Eric Sanchez, Lando Shepherd, Peter Wright

Introduction
We are working on building the interface, data collection, and motion control modules for the HyperRail project, a cross-disciplinary project being conducted by the Openly Published Environmental Sensing (OPEnS) Lab, The OSU Department of Electrical Engineering and Computer Science, and the OSU Department of Biological and Ecological Engineering. The HyperRail is a modular linear motion system designed for low-cost, precision data collection in a variety of plant growing environments.
The HyperRail is an aluminum-framed linear motion device with a gantry-mounted end effector. The gantry moves along the base frame in the Y-direction and the end effector moves along the upper frame in the X-direction. The system is powered by three stepper motors controlled by an ESP-32 microcontroller connected via USB to the control computer [1]. Environmental data will be collected using an SHT-30 temperature/humidity sensor. Light data collection may be added in a later iteration of the system. Images of the test plots will be collected by a MicaSense Red Edge MX multi-spectral camera. The system is controlled by an Nvidia Jetson Nano single board computer running Robot Operating System and hosting the web user interface for the user to input destinations, specify data collection actions, report on machine status, and review prior collected data. Data which has been collected by the system is stored in a SQLite database on the Jetson Nano and stores the data collection events as a series of waypoints represented by an X-Y coordinate, a type of data to be collected, a timestamp, and a unique identifier. A series of waypoints collected together constitutes a program. The user may create a program which they want to run for data collection, run a previously saved program to collect data from the same locations in the test plot over time, or review historical data.

Current Status
To date, we have been focused on on-boarding with the project objectives, the languages involved, and the concepts of ROS. During the first weeks of this term we have focused on the design of the system. At this stage, the program flow has been laid out, message formats for the services and topics have been established, and the basis for nodes has been established. The database schema has been established and in the process of being built. The user interface has been wireframed, UI development has started, and the message protocol for publishing to ROS topics from the Ruby front end has been tested. The framework for the nodes which will handle motion control and interacting with the sensor nodes has been established and the logic for triggering events through services has been started.

Design Discussion

User Interface
Ultimately, the user will send instructions to the HyperRail through a web user interface. A rough wireframe of the UI was created. It includes three main pages. The first page allows the user to move the end effector to a distinct x and y coordinate. It also will show current sensor (temp, co2, etc) data. (also, this might show the current NDVI data from the pictures taken) This display data page enables the user to enter x and y coordinates to move the end effector. It is also used for testing purposes. For the second page, (Path planning) the user may designate a series of waypoints, each with an associated action. Actions at each waypoint can be to collect an image and/or a set of environmental readings. The user may also send individual instructions to the HyperRail to manually move the end effector about the test plot and collect data. When the user enters a series of waypoints, they are saved in a SQLite database stored on the host computer for reference when the program is being executed and data is being collected. The third page is a current display of the location of the end effector. As of right now, simple data such as x and y position of the end effector will be displayed.

ROS Components
The HyperRail control system is built on ROS, a publish/subscribe programing paradigm which consists of a set of concurrently running nodes. In a ROS program, each node is responsible for a specific action. This may be a logical operation on the host computer or interacting with a microcontroller. ROS provides two primary interprocess communication channels for nodes. Services, which allow for one-to-one communication between two nodes in a request/response format and topics which allow for one-to-many communication between multiple nodes in a publish/subscribe format. The HyperRail system will include nodes for data collection, motion control, and location tracking.
Motion control will be handled by a program node, which receives requests from the user interface containing the unique identifier of the program that the user has selected to run. It will then query the database for the waypoints which constitute the program entered by the user. The program node will send the destination to the motion node which will split up the distance between the end effector’s current location and the waypoint destination to generate a series of G-codes and publish them to the G-code topic. The G-code topic is subscribed to by the ESP32controller node which ultimately sends the series of codes over a serial connection to the ESP-32 microcontroller which controls the stepper motors which move the end effector along the tracks. As the end effector is moving, the location node will poll the location of the end effector until the destination is reached. When the destination is reached, the motion node will notify the program node that the destination has been reached. The program node will then send a request to the sensor node or camera node to collect a set of environmental readings or an image at the designated waypoint. In the case of the sensor node, once the data has been collected, it will respond to the program node with the environmental readings for the location to be stored by the program node. In the case of the camera node, the image will be stored to the file system by the camera node directly. Once all responses to data collection requests have been received by the program node, the next waypoint is sent to the motion node. This process will repeat until each waypoint in the program has been visited and the specified data has been collected.
Environmental data will be collected by the sensor node which interacts with an SHT-30 temperature/humidity sensor. This sensor will be connected to the Jetson GPIO and readings collected when the node receives a request from the program node. The sensor service request consists of the unique id for the datapoint and the type of reading to be collected. The response consists of the unique id for the datapoint, a status code, and the results of the readings. When the program node sends a request through the service, the handler function will execute the data collection and send the response. The program node will be responsible for storing the datapoint in the database.
Images will be collected by the camera node which interacts with the MicaSense camera. Similar to the sensor node, the camera node service passes a request from the program node to the camera node with an instruction to collect an image. When the image is collected, the camera node sends a response containing the identifier for the data point, a status code, and the file path which is stored in the database by the program node.

Work to be completed
Over the remainder of the term, we have to fill in the skeleton of the program we have started. In the program node, we still need to write the database queries to retrieve programs from the database and store data collected. The motion and location nodes need to have their services and topics revised to fit a modification to the control flow. The motion node will need to have functionality built to split up the distance between the end effector’s current location and the destination into short segments. The sensor and camera nodes still need to be built. Before this can happen, we will need to discuss the sensor types and connection with the project owners. Once we have this information, we can begin setting up the functions which will collect and return that data to the program node. We still need to get a better understanding of how to interact with the camera in ROS. To do this, we will download sample data from the Micasense website, create experimental ROS nodes that accept the same data type and run some tests. We will also need to understand how to store files to the file system for retrieval later.
The web UI will need to have additional work done to facilitate program creation, display real time machine status, and display/download images take from the Micasense camera. There will also need to be some additional work to send one-off Gcode to the ROS node responsible for sending Gcode to the ESP32 controller. Once it is determined how to stitch images that the Micasense camera generates, there will need to be a script program which can generate, stitch, and use those images in the program editing interface on an ongoing basis. Ideally this entire code path will be tested directly on the Jetson Nano as well as this is a non-standard ARM architecture and there may be additional challenges ensuring all software runs properly on that architecture.
We still need to investigate the Micasense camera in more depth. We need to determine which data we need to retrieve from the micasense and how we can process the images. Also, the photo-stitching needs has not yet started implementation. Both of these features seem to have a scope that is still undefined.

Level of Effort
The complexity of this project warrants a high level of research prior to any experimentation work we have put forth thus far. Initially, it was necessary to learn about the ROS library general as it was new to most if not all of us. We then completed a few tutorials in order to solidify our understanding of the way this library works before we could apply it to the needs of the HyperRail project. Another challenge involved not having the ability to experiment with the hardware as each member of the CS capstone group is remote. With our time spent researching, conducting experiments and having frequent meetings with the project owners to ensure we are on the right path, we thoroughly believe that each member of the group has met or exceeded the 10 hour/ week level of effort.


Figure 1 - Solid Works of Gantry [2]

Diagrams and Research Code

Attached in zipfile:
flowchart of nodes - node_flowchart.pdf wireframe of UI - ui_wireframe.pdf
UML diagram of database - database_schema.pdf

Links:
Testing websocket that connects Interface with ROS nodes - link (https://github.com/Jbruslind/HyperRail/blob/ros_sensor_interpretation/ruby_ros_connection.rb) Javascript ROSBridge connection example - link (https://github.com/pWr1ght/practice_rosbridge_websocket)
Ruby on Rails UI - link (https://github.com/Jbruslind/HyperRail/tree/web-ui/WebUI)

ROS Nodes - LocationTracker, PathPlanner, tester nodes. link (https://github.com/Jbruslind/HyperRail/tree/ros_pathplanning/src/hyper_rail/nodes)

References:
[1] J. M. Lopez Alcala, M. Haagsma, C. J. Udell, and J. S. Selker, “HyperRail: Modular, 3D printed, 1–100 m, programmable, and low-cost linear motion control system for imaging and Sensor Suites,” HardwareX, vol. 6, 2019.
[2] J. Bruslind, https://github.com/Jbruslind/HyperRail/tree/main/Inventor%20Files

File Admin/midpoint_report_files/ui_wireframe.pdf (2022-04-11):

HyperRail Admin (full wireframe-subject to change- based on creation-plan ) (https://docs.google.com/document/d/1EF_tgKIoTAHzGSGNuPoZ6seQw5sl9cmFhcXbk-TkFUs/edit?usp=sharing)

Individual movement commands; submit; Indication that action has been completed; This area gives feeback when cooridinates are reached, in progress, possible error indication.; submitting x and y coordinates possibly disable submit button when gantry is moving or recording other land plots.

Article 2

1. Data Display | 2. Path Planning Programs

Show most recent Picture taken or NDVI (can taken from local file)

CO2: {Co2}
Temp: {Celsius}
Moisture: {g/m³?}

1.

TBD: recent picture or NVDI data

2.

Notes:
-Database: SQLlite3:
database that is local/reliable -Diagrams not to scale
-will probably not implement all this.

Programs; directories to find get data files; Button: adding program to list; Button: edit button to edit path; for a current program, possibly have a button that allows the data to be download for each run.

-Show a list of the programs and possibly allow user to possible download files or the user might go to the

1. Data Display
1. Data Display | 2. Path Planning
3. Edit path program page
2. Path Planning Programs

2

1

3

Find a way to implement editing a path. Possibly for now, we can possible just have a string of coordinates. that we put in.

Possible TODO:
- add Routes
- add Database Variables
-particular buttons might be missing due to features not fully being fleshed out
5. Create path program page
1. Data Display | 2. Path Planning

2

1

3

Find a way to implement creating a path. For now, we can we have a input for coordinates

6. Show current positioning

X: {x-axis}
Y: {y-axis}
System info:
(System info: Build info, voltage / current , PCB / system OS?)

Current positioning and status

6.

1. Data Display | 2. Path Planning Programs | 6. show current positioning
6. show current positioning
6. show current
6. show current positioning

current Sensor Data:

x: {x-axis} y: {y-axis} current positions

For each
coordinate,
there will
be an
action
setup for
each
sensor
reading

For each
coordinate,
there will
be an
action
setup for
each
sensor
reading

Actions
are
reading
data from
sensors,
pictures

Actions
are
reading
data from
sensors,
pictures

*Data Display Page use case: Used for doing individual movements and monitoring the sensor data. Mainly used for testing.

*show current positioning - shows the x,y positioning and current status system info that is to be determined.

*Path planning Page use case: Creates, Edit, Add programs. These programs move the end effector to each waypoint indicated. It will have an action the

Key:
* - indicate use case

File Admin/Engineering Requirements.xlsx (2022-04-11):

Customer Requirement | Engineering Requirement | Verification Process | Verification Method
The system should be accurate. | The system should be accurate to within +- 1% of the workable area |  | Test
The system should be safe. | The system enclosure will not allow any object with a diameter greater than 1mm to enter the enclosure. | The team will produce all mechanical design documents. | Inspection
The system will operate on US standard electricity | The system will operate on a US AC input (120V, 15A) | An electrical inspection will be preformed showing operation at 120V 60Hz | Inspection
The system should be modular | The system will be able to increase / decrease its effective length using a standard kit of parts | A mechanical inspection will be preformed showing continual operation before and after the addition of a modular kit | Inspection
The system will operate over WiFi | The system will be able to accept commands through a wireless protocol | A "common" operation will be preformed using only wireless communication protocols | Test
The system will have automatic path planning | The system will accept user direction commands and determine a path to each destination | A series of points will be input to the system and the end effector will be visually inspected to reach each destination | Inspection
The system software should be easy to use | The system UI will be simple enough so that someone with little to no knowledge of the interface can preform "basic" operations | A user will be found with no prior knowledge of the interface and will be asked to preform a set of tasks. Successful operation meets requirement criteria | Test
The system should be reliable | The system will operate continueously for a minimum of 6 hours
The system should be autonomous | The system will operate normally with no human intervention for 2 hours
The system will provide visual feedback | The system will capture images of the available workspace
The system will have a user interface | The system will accept user commands through an interface system
The system should collect data about its environment | The system will allow for data sampling of environmental factors (TBD) at a rate of 5Hz
The system should make data accessible | The system will make collected data available in a standard format
The system should be safe. | Human accessible electrical inputs will be properly rated for the Human Body Model ESD per JS 001 | A 100pf Capactior in series with a 1500Ohm resistor will be charged to 2kV and will be discharged to the defined accessible inputs
The system should have an emergency shutoff | The system will have a single contact to denergize within 1s of interaction
The System will use commercially available cabling | The system will utilize cabling solutions that can be purchased at nearby hardware stores
The system will use standard structual materials | The system mechanical assembly will contain a minimum of 50% COTS parts by number

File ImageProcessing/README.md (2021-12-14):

This folder contains the image compositor using GraphicsMagick and a prior version of the opencv stitcher to create multiple stitched images.

The compositor combines all images from a run using the X, Y centriods, the camera height, and the field of view.

To use this program:
* Install virtual environment using `pip install -r requirements.txt`
* Activate environment with `source env/bin/activate`
* Execute image processor for a given program_run using `python imageProcessor.py -p {program_run_id}`

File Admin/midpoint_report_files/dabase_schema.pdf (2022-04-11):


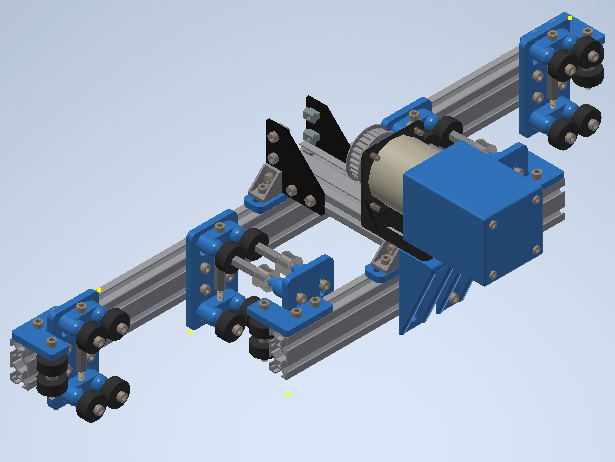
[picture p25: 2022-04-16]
assets/Mechanical_assets/X_Carriage_back.png

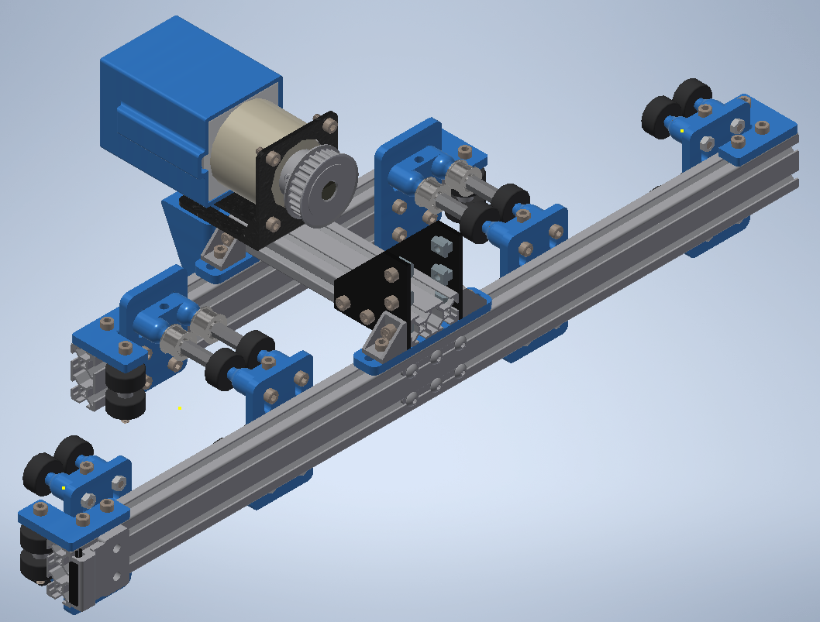
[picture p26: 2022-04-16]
assets/Mechanical_assets/X_Carriage.png

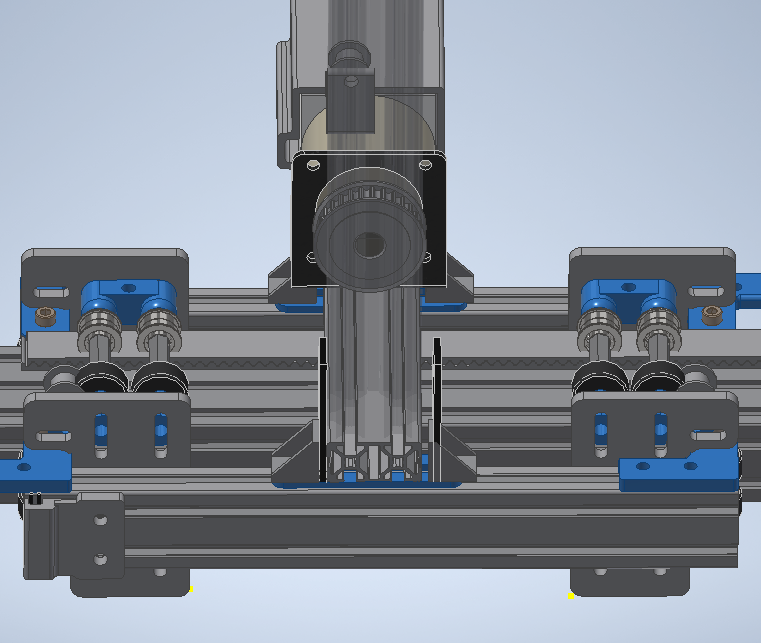
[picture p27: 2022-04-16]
assets/Mechanical_assets/Belleverman_Style.png

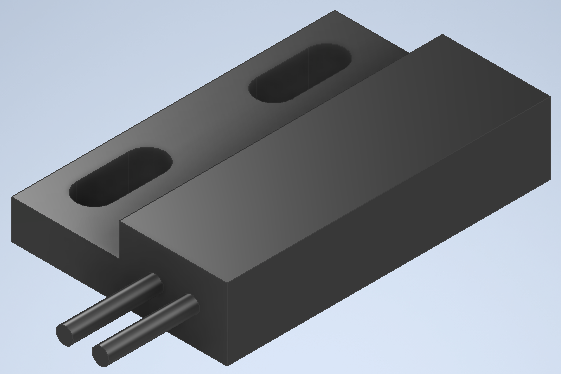
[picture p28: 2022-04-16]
assets/Mechanical_assets/magnet.png

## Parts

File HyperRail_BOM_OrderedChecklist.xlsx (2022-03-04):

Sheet: Overall
Overall Cost
Manufacturer Part Number | Vendor | Customer Reference | Quantity | Unit Price | Extended Price | Quantity Available | Description | Category | Subtotal | $1408.00
 |  | Side Rail Assembly | 2 | $448.25 | $896.50 |  |  | Mechanical
 |  | Top Carriage Assembly | 1 | $261.03 | $261.03 |  |  | Mechanical | MODIFY THESE
 |  |  |  |  |  |  |  | Electrical | Base Parameters |  | Add-On Modules |  | Total |  | (ft)
 |  |  |  |  |  |  |  | Electrical | Height (m) | 1.5 | Height (m) | 1.5 | Height (m) | 1.5 | 4.92126
 |  | ESP32 GRBL Controller PCB | 1 | $34.43 | $34.43 |  |  | Electrical | Width (m) | 2 | Width (m) | 2 | Width (m) | 2 | 6.56168
 |  | Ebox Assembly | 1 | $216.05 | $216.05 |  |  |  | Length (m) | 2 | Length (m) | 2 | Length (m) | 2 | 6.56168
 |  |  |  |  |  |  |  |  |  |  | Number | 0

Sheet: Electrical
Integrated Stepper Driver PCB BOM
Manufacturer Part Number | Manufacturer | Digi-Key Part Number | Customer Reference | Packaging | Part Status | Quantity | Unit Price | Extended Price | Quantity Available | Mfg Std Lead Time | Description | RoHS Status | Lead Free Status | REACH Status | Column1
LTST-C193TBKT-5A | Lite-On Inc. | 160-1827-1-ND | 5V, 24V_ Integrated | Cut Tape (CT) | Active | 2 | $0.30 | $0.60 | 124776 | 20 Weeks | LED BLUE CLEAR CHIP SMD | ROHS3 Compliant | Lead free | Not Available
CL31A106KBHNNNE | Samsung Electro-Mechanics | 1276-2876-1-ND | C1, C2, C9, C11, C12_ Integrated | Cut Tape (CT) | Active | 5 | $0.36 | $1.80 | 1019880 | 28 Weeks | CAP CER 10UF 50V X5R 1206 | ROHS3 Compliant | Lead free | REACH Unaffected
CL10B104JB8NNNC | Samsung Electro-Mechanics | 1276-1033-1-ND | C3, C4, C6, C7, C10_ Integrated | Cut Tape (CT) | Active | 5 | $0.10 | $0.50 | 354161 | 28 Weeks | CAP CER 0.1UF 50V X7R 0603 | ROHS3 Compliant | Lead free | REACH Unaffected
0603B223K500CT | Walsin Technology Corporation | 1292-1417-1-ND | C5_ Integrated | Cut Tape (CT) | Active | 1 | $0.10 | $0.10 | 233944 | 21 Weeks | CAP CER 0.022UF 50V X7R 0603 | ROHS3 Compliant | Lead free | REACH Unaffected
CL31B475KBHNNNE | Samsung Electro-Mechanics | 1276-2789-1-ND | C8_ Integrated | Cut Tape (CT) | Active | 1 | $0.36 | $0.36 | 613293 | 28 Weeks | CAP CER 4.7UF 50V X7R 1206 | ROHS3 Compliant | Lead free | REACH Unaffected
54602-908LF | Amphenol ICC (FCI) | 609-1046-ND | J1_ Integrated | Bulk | Active | 1 | $0.66 | $0.66 | 70638 | 11 Weeks | CONN MOD JACK 8P8C R/A UNSHLD | RoHS Compliant | Lead free | REACH Unaffected
54601-906WPLF | Amphenol ICC (FCI) | 609-4729-ND | J2_ Integrated | Bulk | Active | 1 | $0.44 | $0.44 | 2517 | 18 Weeks | CONN MOD JACK 6P6C R/A UNSHLD | RoHS Compliant | Lead free | REACH Unaffected
OSTTE040161 | On Shore Technology Inc. | ED2637-ND | J3_ Integrated | Bulk | Active | 1 | $1.02 | $1.02 | 3260 | 10 Weeks | TERM BLK 4POS SIDE ENT 3.5MM PCB | ROHS3 Compliant | Lead free | REACH Unaffected
ERJ-6DSFR11V | Panasonic Electronic Components | P19309CT-ND | R1, R2_ Integrated | Cut Tape (CT) | Active | 2 | $0.45 | $0.90 | 3823 | 28 Weeks | RES 0.11 OHM 1% 1/2W 0805 | ROHS3 Compliant | Lead free | REACH Unaffected
RC0603FR-0720KL | Yageo | 311-20.0KHRCT-ND | R3, R5, R6, R7, R8, R9_ Integrated | Cut Tape (CT) | Active | 6 | $0.10 | $0.60 | 2708711 | 20 Weeks | RES SMD 20K OHM 1% 1/10W 0603 | ROHS3 Compliant | Lead free | REACH Unaffected
TC33X-2-203E | Bourns Inc. | TC33X-2-203ECT-ND | R4_ Integrated | Cut Tape (CT) | Active | 1 | $0.26 | $0.26 | 0 | 18 Weeks | TRIMMER 20K OHM 0.1W J LEAD TOP | ROHS3 Compliant | Lead free | REACH Unaffected
RMCF0603FT4K70 | Stackpole Electronics Inc | RMCF0603FT4K70CT-ND | R19_ Integrated | Cut Tape (CT) | Active | 1 | $0.10 | $0.10 | 2509617 | 21 Weeks | RES 4.7K OHM 1% 1/10W 0603 | ROHS3 Compliant | Lead free | REACH Unaffected
CRGCQ0603J470R | TE Connectivity Passive Product | A130089CT-ND | R20_ Integrated | Cut Tape (CT) | Active | 1 | $0.10 | $0.10 | 83167 | 19 Weeks | CRGCQ 0603 470R 5% | RoHS Compliant | Lead free | Not Available
1825057-3 | TE Connectivity ALCOSWITCH Switches | 450-1364-ND | SW1_ Integrated | Tube | Active | 1 | $0.93 | $0.93 | 4541 | 23 Weeks | SWITCH SLIDE DIP SPST 100MA 24V | RoHS Compliant | Lead free | Not Available
AS5047P-ATSM | ams | AS5047P-ATSMCT-ND | U1_ Integrated | Cut Tape (CT) | Active | 1 | $0.00 | $0.00 | 1001 | 14 Weeks | ROTARY ENCODER MAGNETIC PROG | RoHS Compliant | Lead free | REACH Unaffected | ENCODER OMITTED FROM ASSEMBLY
TMC2209-LA-T | Trinamic Motion Control GmbH | 1460-1398-1-ND | U2_ Integrated | Cut Tape (CT) | Active | 1 | $2.74 | $2.74 | 0 | 6 Weeks | IC MTR DRV 4.75-28V QFN28 | ROHS3 Compliant | Lead free | Not Available
LMZM23601V5SILR | Texas Instruments | 296-LMZM23601V5SILRCT-ND | U3_ Integrated | Cut Tape (CT) | Active | 1 | $5.69 | $5.69 | 3465 | 8 Weeks | DC DC CONVERTER 5V | ROHS3 Compliant | Lead free | REACH Unaffected
MBR0520LT1G | ON Semiconductor | MBR0520LT1GOSCT-ND | VD1, VD2_ Integrated | Cut Tape (CT) | Active | 2 | $0.34 | $0.68 | 0 | 21 Weeks | DIODE SCHOTTKY 20V 500MA SOD123 | ROHS3 Compliant | Lead free | REACH Unaffected
Subtotal |  |  |  |  |  |  |  | $17.48
ESP32 GRBL Controller PCB BOM
Manufacturer Part Number | Manufacturer | Digi-Key Part Number | Customer Reference | Packaging | Part Status | Quantity | Unit Price | Extended Price | Quantity Available | Mfg Std Lead Time | Description | RoHS Status | Lead Free Status | REACH Status
LTST-C193TBKT-5A | Lite-On Inc. | 160-1827-1-ND | 3_3V, 5V, 24V | Cut Tape (CT) | Active | 3 | $0.30 | $0.90 | 124776 | 20 Weeks | LED BLUE CLEAR CHIP SMD | ROHS3 Compliant | Lead free | Not Available
TAP106K025SCS | AVX Corporation | 478-1841-ND | C1, C2, C3 | Bulk | Active | 3 | $0.82 | $2.46 | 792 | 21 Weeks | CAP TANT 10UF 10% 25V RADIAL | ROHS3 Compliant | Lead free | REACH Unaffected
C1206C104K5RAC7800 | KEMET | 399-C1206C104K5RAC7800CT-ND | C4, C6 | Cut Tape (CT) | Active | 2 | $0.11 | $0.22 | 936348 | 15 Weeks | CAP CER 0.1UF 50V X7R 1206 | ROHS3 Compliant | Lead free | REACH Unaffected
CL31B105KOFNNNE | Samsung Electro-Mechanics | 1276-1783-1-ND | C5 | Cut Tape (CT) | Active | 1 | $0.15 | $0.15 | 157643 | 28 Weeks | CAP CER 1UF 16V X7R 1206 | ROHS3 Compliant | Lead free | REACH Unaffected
CL31A106KBHNNNE | Samsung Electro-Mechanics | 1276-2876-1-ND | C11, C12 | Cut Tape (CT) | Active | 2 | $0.36 | $0.72 | 1019880 | 28 Weeks | CAP CER 10UF 50V X5R 1206 | ROHS3 Compliant | Lead free | REACH Unaffected
690-005-299-043 | EDAC Inc. | 151-1206-1-ND | J | Cut Tape (CT) | Active | 1 | $0.54 | $0.54 | 78973 | 17 Weeks | CONN RCPT USB2.0 MINI B SMD R/A | ROHS3 Compliant | Lead free | REACH Unaffected
54602-908LF | Amphenol ICC (FCI) | 609-1046-ND | J1, J2, J3, J4, J5, J6 | Bulk | Active | 6 | $0.66 | $3.96 | 70638 | 11 Weeks | CONN MOD JACK 8P8C R/A UNSHLD | RoHS Compliant | Lead free | REACH Unaffected
OSTTA020161 | On Shore Technology Inc. | ED2561-ND | J7, J8, J9, J10, J11, J12, VIN (12 - 24V) | Bulk | Active | 10 | $0.42 | $4.22 | 26800 | 11 Weeks | TERM BLK 2POS SIDE ENTRY 5MM PCB | ROHS3 Compliant | Lead free | REACH Unaffected
5040771891 | Molex | WM9315CT-ND | J13 | Cut Tape (CT) | Active | 1 | $2.02 | $2.02 | 2400 | 17 Weeks | CONN MICRO SD CARD PUSH-PULL R/A | ROHS3 Compliant | Lead free | REACH Unaffected
ESP32-WROOM-32E (8MB) | Espressif Systems | 1965-ESP32-WROOM-32E(8MB)CT-ND | M1 | Cut Tape (CT) | Active | 1 | $3.30 | $3.30 | 521 | 8 Weeks | RX TXRX MOD WIFI TRACE ANT SMD | Not Available | Not Available | Not Available
MBT2222ADW1T1G | ON Semiconductor | MBT2222ADW1T1GOSCT-ND | Q1 | Cut Tape (CT) | Active | 1 | $0.26 | $0.26 | 246 | 36 Weeks | TRANS 2NPN 40V 0.6A SC88/SC70-6 | ROHS3 Compliant | Lead free | REACH Unaffected
ERJ-6GEYJ822V | Panasonic Electronic Components | P8.2KACT-ND | R1, R2, R3, R4, R5, R6, R7, R8, R9, R10, R11, R1 | Cut Tape (CT) | Active | 19 | $0.06 | $1.08 | 24018 | 22 Weeks | RES SMD 8.2K OHM 5% 1/8W 0805 | ROHS3 Compliant | Lead free | REACH Unaffected
RMCF0603FT4K70 | Stackpole Electronics Inc | RMCF0603FT4K70CT-ND | R19 | Cut Tape (CT) | Active | 1 | $0.10 | $0.10 | 2509617 | 21 Weeks | RES 4.7K OHM 1% 1/10W 0603 | ROHS3 Compliant | Lead free | REACH Unaffected
CRGCQ0603J470R | TE Connectivity Passive Product | A130089CT-ND | R20 | Cut Tape (CT) | Active | 1 | $0.10 | $0.10 | 83167 | 19 Weeks | CRGCQ 0603 470R 5% | RoHS Compliant | Lead free | Not Available
RC0603FR-07150RL | Yageo | 311-150HRCT-ND | R22 | Cut Tape (CT) | Active | 1 | $0.10 | $0.10 | 1050240 | 20 Weeks | RES SMD 150 OHM 1% 1/10W 0603 | ROHS3 Compliant | Lead free | REACH Unaffected
1825910-6 | TE Connectivity ALCOSWITCH Switches | 450-1650-ND | S1, S2 | Bulk | Active | 2 | $0.10 | $0.20 | 67015 | 17 Weeks | SWITCH TACTILE SPST-NO 0.05A 24V | RoHS Compliant | Lead free | Not Available
LM1117MPX-ADJ/NOPB | Texas Instruments | LM1117MPX-ADJ/NOPBCT-ND | U1 | Cut Tape (CT) | Active | 1 | $1.17 | $1.17 | 0 | 12 Weeks | IC REG LIN POS ADJ 800MA SOT223 | ROHS3 Compliant | Lead free | REACH Unaffected
LMZM23601V5SILR | Texas Instruments | 296-LMZM23601V5SILRCT-ND | U2 | Cut Tape (CT) | Active | 1 | $5.69 | $5.69 | 3465 | 8 Weeks | DC DC CONVERTER 5V | ROHS3 Compliant | Lead free | REACH Unaffected
SN74AHCT595D | Texas Instruments | 296-14308-5-ND | U3, U4, U6 | Tube | Active | 3 | $0.69 | $2.07 | 932 | 6 Weeks | IC 8-BIT SHIFT REGISTER 16-SOIC | ROHS3 Compliant | Lead free | REACH Unaffected
SN74LVC3G14DCUT | Texas Instruments | 296-32334-1-ND | U7 | Cut Tape (CT) | Active | 1 | $0.95 | $0.95 | 833 | 6 Weeks | IC INVERT SCHMITT 3CH 3IN 8VSSOP | ROHS3 Compliant | Lead free | REACH Unaffected
MBR0520LT1G | ON Semiconductor | MBR0520LT1GOSCT-ND | VD1, VD2 | Cut Tape (CT) | Active | 2 | $0.34 | $0.68 | 0 | 21 Weeks | DIODE SCHOTTKY 20V 500MA SOD123 | ROHS3 Compliant | Lead free | REACH Unaffected
CP2102-GMR | Silicon Labs | 336-1160-1-ND | U5 | Cut Tape (CT) | Not For New Designs | 1 | $3.54 | $3.54 | 3335 | 20 Weeks | IC USB-TO-UART BRIDGE 28VQFN | ROHS3 Compliant | Lead free | Not Available
Subtotal |  |  |  |  |  |  |  | $34.43
Main System Assembly
Manufacturer Part Number | Manufacturer | Digi-Key Part Number | Customer Reference | Packaging | Part Status | Quantity | Unit Price | Extended Price | Quantity Available | Mfg Std Lead Time | Description | RoHS Status | Lead Free Status | REACH Status
BC-5SE100M | Bel Inc. | 1847-1059-ND | Motor Connector Wire (30ft) | Bulk | Active | 4 | $11.63 | $46.52 | 40 | 18 Weeks | CABLE MOD 8P8C PLUG-PLUG 32.81' | RoHS Compliant | Lead free | Not Available
945-13541-0000-000 | Nvidia |  | Main SBC | Box | Active | 1 | $59.00 | $59.00 | 2 |  | Single Board Computer, NVidia Jetson Nano 2GB Development Kit | ROHS3 Compliant | Lead free | Not Available
Subtotal |  |  |  |  |  |  |  | $105.52

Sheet: Mechanical - Rail_AssemblyV2_0
Rail_AssemblyV2_0
Part Number - Assembly | Thumbnail | Quantity | Vendor | Vendor Link | Unit Price | Extended Price | Description | Comments | Alternative Vendor | Alternative Vendor Link | SubTotal
23HS8430B |  | 1 | Stepper Online | StepperOnline (https://bit.ly/3vasq0u) | $54.77 | $54.77 | NEMA 23 Motor w/ Planetary Gearbox (47:1 reduction) | Bought as a pack (both motor and gearbox) |  |  | $448.25
2804S_NEMA2115_1Gearbox |  | 1 | Stepper Online |  | $0.00 | $0.00 | Included with 23HS8430B | Gearbox included in motor price
Main |  | 1 | Custom - Electronics |  | $17.48 | $17.48 | Integrated Stepper Driver custom PCB with closed feedback option | Custom assembly / manufacter - see Electrical tab
20-4040_2m |  | 1 | 8020 | 20-4040 (https://8020.net/20-4040.html) | $53.69 | $53.69 | 20-2040 is a 20mm x 40mm metric 20 series rectangular T-slot profile | 2 meter cut length (can be customized for different track requirements)
NEMA23_Shroud |  | 1 | Amazon | PETG (https://amzn.to/3p4Z7Zp) | $1.56 | $1.56 | Right Angle Bracket for wheel axis - 3D printed with PETG (price estimated on $/Kg for PETG on Amazon | * Price is estimated based on Cura Slicer weight estimates for 3D printed part and $/Kg of Amazon Basics PETG Filament
98952A059_ALUM MALE-FEM THRDED HEX STANDOFF |  | 8 | McMaster | McMaster (https://www.mcmaster.com/98952A059/) | $2.81 | $22.48
95783A039_NYLON 6-6 MALE-FEM THRDED HEX STANDOFF |  | 4 | McMaster | McMaster (https://www.mcmaster.com/95783A039/) | $3.00 | $12.00
HFS5-4060-2125 |  | 1 | Misumi | Misumi (https://bit.ly/3Hc5Mr5) | $46.32 | $46.32 | 2125mm HFS5-4060 Tslot Extrusion
Integrated_Stepper_NEMA23_Mount |  | 1 | Amazon | PETG (https://amzn.to/3p4Z7Zp) | $0.15 | $0.15 | Custom motor bracket adapter for the Integrated Stepper PCB onto NEMA 23 Motors | * Price is estimated based on Cura Slicer weight estimates for 3D printed part and $/Kg of Amazon Basics PETG Filament
20-2568_d |  | 1 | 8020 | 8020 (https://8020.net/20-2568.html) | $28.24 | $28.24
5mm_bore_10mm_width_idlepulley |  | 1 | Amazon | Amazon (https://www.amazon.com/gp/product/B07CXNK33Q/ref=ppx_yo_dt_b_search_asin_title?ie=UTF8&psc=1) | $2.50 | $2.50 | GT2 Idler Pulley 20 Toothless 3mm Bore 10mm Width | Bought as a pack of 10
Tape_Belt_Layer |  | 1 | Amazon | PETG (https://amzn.to/3p4Z7Zp) | $0.34 | $0.34 | Right Angle Bracket for wheel axis - 3D printed with PETG (price estimated on $/Kg for PETG on Amazon | * Price is estimated based on Cura Slicer weight estimates for 3D printed part and $/Kg of Amazon Basics PETG Filament
SDP_sdpsi_a_6a55m028df0912 |  | 1 | SDP/SI | SDPSI (https://shop.sdp-si.com/catalog/product/?id=A_6A55M028DF0912) | $16.04 | $16.04
SDP_sdpsi_a_6r25mc1000 |  | 1 | PolyBelt | PolyBelt (https://bit.ly/3BHYvxY) | $20.50 | $20.50 | 15-5M MTD5 Open End Belt Roll Polyurethane with Steel Cords. | Can also be bought on Ebay / Amazon for much cheapera but shipping time is not guarenteed | Ebay | Ebay (https://www.ebay.com/itm/382865666347?var=651553605528)
Carriage_Assembly |  | 1 | Custom |  | $107.98 | $107.98 | Custom Carriage Assembly
NEMA23_StepperonlineMount |  | 1 | Stepper Online | Stepper Online (https://bit.ly/3payYID) | $1.84 | $1.84 | Nema 23 Motor Mount Bracket
59145_Sensor |  | 1 | Digikey | Digikey (https://www.digikey.com/en/products/detail/littelfuse-inc/59145-040/4771993) | $4.95 | $4.95 | SENSOR REED SW SPST-NC W LEADS
RightAngle_SideBracket |  | 4 | Amazon | Amazon (https://amzn.to/35hVTdS) | $1.69 | $6.76 | 2020 Corner Bracket Plate Anodised L Shape 5 Hole
Cable_Guide_Holder |  | 6 | Amazon | PETG (https://amzn.to/3p4Z7Zp) | $0.25 | $1.48 | Cable holder for Power cabling - 3D printed with PETG (price estimated on $/Kg for PETG on Amazon | * Price is estimated based on Cura Slicer weight estimates for 3D printed part and $/Kg of Amazon Basics PETG Filament
RightAngle_PulleySupport |  | 1 | Amazon | PETG | $0.23 | $0.23 | Bracket to hold idler pulley for tension adjust - 3D printed with PETG (price estimated on $/Kg for PETG on Amazon | * Price is estimated based on Cura Slicer weight estimates for 3D printed part and $/Kg of Amazon Basics PETG Filament
MagnetHolder |  | 1 | Amazon | PETG | $0.21 | $0.21 | Magnet Holder for End Stops - 3D printed with PETG (price estimated on $/Kg for PETG on Amazon | * Price is estimated based on Cura Slicer weight estimates for 3D printed part and $/Kg of Amazon Basics PETG Filament
MagnetActuatorHolder |  | 1 | Amazon | PETG | $0.30 | $0.30 | Magnet Holder for End Stops - 3D printed with PETG (price estimated on $/Kg for PETG on Amazon | * Price is estimated based on Cura Slicer weight estimates for 3D printed part and $/Kg of Amazon Basics PETG Filament
59145_Actuator |  | 1 | Digikey | Digikey (https://www.digikey.com/en/products/detail/littelfuse-inc/57145-000/43980) | $3.06 | $3.06
Bottom_Foot_Assembly |  | 3 | Custom |  | $6.87 | $20.60 | Custom foot for leveling track frame
Bolt M5 8mm |  | 18 | McMaster | McMaster (https://www.mcmaster.com/92095A207/) | $0.16 | $2.94 | Passivated 18-8 Stainless Steel, M5 x 0.80 mm Thread, 8mm Long
Bolt M5 12mm |  | 8 | McMaster | McMaster (https://www.mcmaster.com/92095A210/) | $0.20 | $1.60 | Passivated 18-8 Stainless Steel, M5 x 0.80 mm Thread, 12mm Long
Bolt M5 25mm |  | 1 | McMaster | McMaster (https://www.mcmaster.com/92095A216/) | $0.31 | $0.31 | Passivated 18-8 Stainless Steel, M5 x 0.80 mm Thread, 25mm Long
Bolt M4 10mm |  | 4 | McMaster | McMaster (https://www.mcmaster.com/94500A227/) | $0.15 | $0.62 | M4 x 0.7mm Thread, 10mm Long
RightAngle_Bracket_60mm |  | 2 | Amazon | PETG (https://amzn.to/3p4Z7Zp) | $0.47 | $0.95 | Right Angle Bracket for wheel axis - 3D printed with PETG (price estimated on $/Kg for PETG on Amazon | * Price is estimated based on Cura Slicer weight estimates for 3D printed part and $/Kg of Amazon Basics PETG Filament
Bolt M5 10mm |  | 4 | McMaster | McMaster (https://www.mcmaster.com/92095A208/) | $0.16 | $0.65 | Passivated 18-8 Stainless Steel, M5 x 0.80 mm Thread, 10mm Long | Bought as a pack of 100 | Amazon | Amazon (https://amzn.to/3I9bwDb)
DIN 508, T-Slot Nut M5 |  | 19 | Amazon | Amazon (https://amzn.to/3I8VKIx) | $0.22 | $4.18 | 2020 Series M5 Half Round Roll in Spring T Nuts | Can be bought on Mcmaster for 5x the price | McMaster | McMaster (https://www.mcmaster.com/90510A232/)
Nut M5 |  | 1 | McMaster | McMaster (https://www.mcmaster.com/90591A260/) | $0.04 | $0.04 | Zinc-Plated Steel Hex Nut, Medium-Strength, Class 8, M5 x 0.8 mm Thread | Should be Zinc plated or Stainless steel for rust prevention, Bought as a pack of 100 |  | Amazon (https://amzn.to/3v5pm5K)
Closed Loop Belt | Not Modeled | 1 | PolyBelt | PolyBelt (https://shop.polybelt.com/650-5m-09-Urethane-Steel-Timing-Belt-130-Tooth-B650-5M-09CPS.htm) | $13.50 | $13.50 | 650-5M-09 Polyurethane with Steel Cord Timing Belt, 650mm Long, 130 Tooth

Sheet: Mechanical - Ebox_Assy
Ebox_Assy
Part Number - Assembly | Thumbnail | Quantity | Vendor | Vendor Link | Unit Price | Extended Price | Description | Comments | Alternative Vendor | Alternative Vendor Link | SubTotal
Main |  | 1 | Custom |  | $34.43 | $34.43 | GRBL ESP32 Controller for Stepper control |  |  |  | $216.05
Jetson nano_fixed |  | 1 | Nvidia | Nvidia (https://developer.nvidia.com/embedded/jetson-nano-2gb-developer-kit) | $59.99 | $59.99
IEC320-C14 |  | 1 | Amazon | Amazon (https://amzn.to/3t85BIe) | $4.00 | $4.00
se300-t-b |  | 1 | Seahorse | Seahorse (https://bit.ly/3pgw6dg) | $27.21 | $27.21
Waterproof Ethernet RJ45 Passthrough |  | 6 | Amazon | Amazon (https://amzn.to/3JW5hmK) | $5.40 | $32.39
DELL_DA-130PE1-00 |  | 1 | Amazon | Amazon (https://amzn.to/3JNUvPk) | $28.49 | $28.49
PowerBrick_Clamp |  | 2 | Amazon | PETG (https://amzn.to/3p4Z7Zp) | $0.27 | $0.53 | Bracket to hold Power Adapter
12_24_5VUSBConverter |  | 1 | Amazon | Amazon (https://amzn.to/3M5yQ72) | $7.00 | $7.00
25W_1224_5V |  | 1 | Amazon | Amazon (https://amzn.to/35rtwKr) | $11.99 | $11.99
EboxBottom |  | 1 | Amazon | PETG (https://amzn.to/3p4Z7Zp) | $0.51 | $0.51 | Plate for X Carriage Wheels | Can also be bought on Amazon for cheaper (quality not guaranteed) | Amazon
95783A051_Nylon 6 6 Male-Female Threaded Hex Standoff |  | 4 | Amazon | Amazon (https://amzn.to/35x7YMk) | $0.08 | $0.32
95783A057_Nylon 6 6 Male-Female Threaded Hex Standoff |  | 8 | Amazon | Amazon (https://amzn.to/359tuHm) | $0.14 | $1.12
95783A069_Nylon 6 6 Male-Female Threaded Hex Standoff |  | 4 | Amazon | Amazon (https://amzn.to/3HoIvlN) | $0.33 | $1.31
Jetson_Mount |  | 1 | Amazon | PETG (https://amzn.to/3p4Z7Zp) | $0.82 | $0.82 | Plate to Mount Jetson
ESP32GRBL_Mount |  | 1 | Amazon | PETG (https://amzn.to/3p4Z7Zp) | $0.82 | $0.82 | Plate to Mount ESP32 Board
Bolt M3 10mm |  | 14 | McMaster | McMaster (https://www.mcmaster.com/94500A223/) | 0.1068 | $1.50
98952A407_Aluminum Male-Female Threaded Hex Standoff |  | 2 | Amazon | Amazon (https://amzn.to/3pifPEE) | $0.32 | $0.65
EboxTslotMount |  | 2 | Amazon | PETG (https://amzn.to/3p4Z7Zp) | $0.51 | $1.03 | Plate for X Carriage Wheels
M5-6mm-HeatInsert |  | 4 | Amazon | Amazon (https://amzn.to/3slfva4) | $0.09 | $0.38
Bolt M5 20mm |  | 2 | McMaster | McMaster (https://www.mcmaster.com/92095A216/) | $0.31 | $0.61 | Passivated 18-8 Stainless Steel, M5 x 0.80 mm Thread, 25mm Long
Bolt M5 10mm |  | 6 | McMaster | McMaster (https://www.mcmaster.com/92095A208/) | $0.16 | $0.98 | Passivated 18-8 Stainless Steel, M5 x 0.80 mm Thread, 10mm Long | Bought as a pack of 100 | Amazon | Amazon (https://amzn.to/3I9bwDb)

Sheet: Mechanical - Top_Rail_Full
Top_Rail_Full
Part Number - Assembly | Thumbnail | Quantity | Vendor | Vendor Link | Unit Price | Extended Price | Description | Comments | Alternative Vendor | Alternative Vendor Link | SubTotal
Top_Rail_Section |  | 1 | Custom |  | $60.72 | $60.72 | Feet mounts (made for M6 caster feet) |  |  |  | $261.03
MagnetActuatorHolder |  | 1 | Amazon | PETG (https://amzn.to/3p4Z7Zp) | $0.30 | $0.30 | Magnet Holder for End Stops - 3D printed with PETG (price estimated on $/Kg for PETG on Amazon | * Price is estimated based on Cura Slicer weight estimates for 3D printed part and $/Kg of Amazon Basics PETG Filament
59145_Sensor |  | 1 | Digikey | Digikey (https://www.digikey.com/en/products/detail/littelfuse-inc/59145-040/4771993) | $4.95 | $4.95 | SENSOR REED SW SPST-NC W LEADS
7959K23_1 2 Width MXL Series No. Ll050mxl Timing Belt_20ft |  | 1 | Amazon | Amazon (https://amzn.to/3pcFWwW) | $3.40 | $3.40 | Passivated 18-8 Stainless Steel, M5 x 0.80 mm Thread, 40mm Long | Should be Zinc plated or Stainless steel for rust prevention, Bought as a pack of 100 | Amazon | Amazon (https://amzn.to/35ijWtt)
CableChain_Holder |  | 10 | Amazon | PETG (https://amzn.to/3p4Z7Zp) | $0.25 | $2.47 | Cable Holder for side track- 3D printed with PETG (price estimated on $/Kg for PETG on Amazon | * Price is estimated based on Cura Slicer weight estimates for 3D printed part and $/Kg of Amazon Basics PETG Filament |  | Amazon (https://amzn.to/3JKgFBP)
YAxis_Carriage |  | 1 | Custom |  | $189.19 | $189.19
Subtotal |  |  |  |  |  |  |  | $261.03

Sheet: Mechanical - Carriage Assembly
Carriage Assembly
Part Number - Assembly | Thumbnail | Quantity | Vendor | Vendor Link | Unit Price | Extended Price | Description | Comments | Alternative Vendor | Alternative Vendor Link | SubTotal
20-2040_150mm |  | 1 | 8020 | 20-2040 (https://8020.net/20-2040.html) | $4.74 | $4.74 | 20-2040 is a 20mm x 40mm metric 20 series rectangular T-slot profile | Can also be bought on Amazon for cheaper (quality not guaranteed) | Amazon | Amazon (https://www.amazon.com/Aluminum-Extrusion-European-Standard-Anodized/dp/B08CN92SP1) | $107.98
14056_m |  | 4 | 8020 | 14056 (https://8020.net/20-2040.html) | 1.94 | $7.76 | The 2 hole - 20mm slotted inside corner bracket with dual support is an external, die-cast fastening method that creates a 90 degree connection | Can be bought on Amazon as a pack of 50 for cheaper per/unit | Amazon | Amazon (https://www.amazon.com/Aluminum-Extrusion-Corner-Bracket-Profile/dp/B08N16BKQS)
Buffer |  | 2 | Custom |  | $2.39 | $4.79 | Buffer used on the side of the carriage to prevent track jumps | Custom Assembly
Carriage_Horizontal_Spacer |  | 2 | Amazon | PETG (https://amzn.to/3p4Z7Zp) | 0.24 | $0.48 | 6mm Spacer to keep horizontal 150mm 2040 from touching lower belt | * Price is estimated based on Cura Slicer weight estimates for 3D printed part and $/Kg of Amazon Basics PETG Filament
20-2040_300mm |  | 3 | 8020 | 20-2040 (https://8020.net/20-2040.html) | $6.98 | $20.94 | 20-2040 is a 20mm x 40mm metric 20 series rectangular T-slot profile | Can also be bought on Amazon for cheaper (quality not guaranteed) |  | Amazon (https://www.amazon.com/European-Standard-Anodized-Aluminum-Extrusion/dp/B099N9QCTJ)
hex spacer standoff nut M5 L30 |  | 4 | DigiKey | DigiKey (https://www.digikey.com/en/products/detail/w%C3%BCrth-elektronik/970300581/6174852) | $0.76 | $3.04 | 18-8 Stainless Steel, 10mm Hex, 30mm Long, M5 x 0.8mm Thread |  |  | Amazon
Buffer_L |  | 2 | Custom |  | $2.39 | $4.79 | Exact same parts as the Buffer, but the screw is flipped so it's Left-Handed rather than Right-Handed | Custom Assembly |  | Amazon
Bolt M5 10mm |  | 36 | McMaster | McMaster (https://www.mcmaster.com/92095A208/) | $0.16 | $5.88 | Passivated 18-8 Stainless Steel, M5 x 0.80 mm Thread, 10mm Long | Bought as a pack of 100 | Amazon | Amazon (https://amzn.to/3I9bwDb)
DIN 508, T-Slot Nut M5 |  | 40 | Amazon | Amazon (https://amzn.to/3I8VKIx) | $0.22 | $8.79 | 2020 Series M5 Half Round Roll in Spring T Nuts | Can be bought on Mcmaster for 5x the price | McMaster | McMaster (https://www.mcmaster.com/90510A232/)
5537T425_T-SLOTTED FRAMING |  | 2 | McMaster | McMaster (https://www.mcmaster.com/5537T425/) | $1.76 | $3.52 | End-Feed Triple Nut, M5 Thread Size | Bought as a pack of 4. BE VERY CAREFUL WITH THE AMAZON ALTERNATIVES THEY SOMETIMES DON'T FIT | Amazon | Amazon (https://amzn.to/3s5sT1T)
X_CarriageFWD_V2_1 |  | 2 | Custom |  | $7.36 | $14.72 | Long plate for gripping Closed Belt structure |  |  | Amazon
X_CarriageFWDBearing_V2_1_Short |  | 2 | Custom |  | $6.50 | $13.00 | Short plate for supporting main frame |  |  | Amazon
X_CarriageBWD_V2_0 |  | 2 | Custom |  | $7.36 | $14.72 | Same as FWD Carriage Plate but this has 2 more M5 nuts and the top screws are reversed |  |  | Amazon
Bolt M5 12mm |  | 4 | McMaster | McMaster (https://www.mcmaster.com/92095A210/) | $0.20 | $0.80 | Passivated 18-8 Stainless Steel, M5 x 0.80 mm Thread, 12mm Long | Bought as a pack of 50

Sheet: Mechanical - Top_Rail_Section
Top_Rail_Section
Part Number - Assembly | Thumbnail | Quantity | Vendor | Vendor Link | Unit Price | Extended Price | Description | Comments | Alternative Vendor | Alternative Vendor Link | SubTotal
5537T425_T-SLOTTED FRAMING |  | 4 | McMaster | McMaster (https://www.mcmaster.com/5537T425/) | $1.76 | $7.03 | End-Feed Triple Nut, M5 Thread Size | Bought as a pack of 4. BE VERY CAREFUL WITH THE AMAZON ALTERNATIVES THEY SOMETIMES DON'T FIT | Amazon | Amazon (https://amzn.to/3s5sT1T) | $60.72
20-4040_2m |  | 1 | 8020 | 20-4040 (https://8020.net/20-4040.html) | $53.69 | $53.69 | 20-2040 is a 40mm x 40mm metric 20 series rectangular T-slot profile | Can also be bought on Amazon for cheaper (quality not guaranteed)
Subtotal |  |  |  |  |  |  |  | $60.72
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

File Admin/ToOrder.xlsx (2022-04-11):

Date needed | Shipping | Requester | Source | Description | Units | Part number | Price/unit | Total | Purpose: X for Y | Notes | Project
 | Jorian Bruslind | Jorian | Amazon (https://amzn.to/3CVQrss) | 10mm x 11mm Drag Chain (1M) | 6 | B07QLGWQ1L | $13.49 | $80.94 | Drag chain for upper axis |  | HyperRail | SubTotal | $139.04
 | Jorian Bruslind | Jorian | Amazon (https://amzn.to/3IdkJLh) | 5 Hole 90 Degree Joint Board Plate | 2 | XC5299 | $9.99 | $19.98 | Extra mounts for gantry |  | HyperRail
 | Jorian Bruslind | Jorian | Amazon (https://amzn.to/3FTulsr) | 100pcs M5 2020 Spring Nut | 1 | B07VHNGBWJ | $16.68 | $16.68 | More mounting equipment |  | HyperRail
 | Jorian Bruslind | Jorian | Amazon (https://amzn.to/3rq3HDk) | IEC 320 C14 Panel Mount Plug | 1 | B082ZFRV1B | $8.49 | $8.49 | Plug for Ebox housing |  | HyperRail
 | Jorian Bruslind | Jorian | Amazon (https://amzn.to/3d0jsbM) | MG Chemicals - 419D-55ML 419D Premium Acrylic Conformal Coating | 1 | B07B8RY7M6 | $12.95 | $12.95 | Conformal Coating for PCBs |  | HyperRail

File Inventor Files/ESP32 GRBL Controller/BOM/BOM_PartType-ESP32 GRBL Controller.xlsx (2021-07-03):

Comment | Description | Designator | Manufacturer Part Number | Quantity
Lite-On LTST-C193TBKT-5A | Blue 1.6 x 0.8 mm (0603) 130 º Intensity Min 11.2 mcd Typical 15 mcd SMT LED | 1, 2, 3 | LTST-C193TBKT-5A | 3
10uF | Capacitor Tantalum Solid 10uF 25V 10% (5.5 X 9mm) Radial 2.5mm 2.5 Ohm 125C Bulk | C1, C3 | TAP106K025SCS | 2
.1uF | Cap Ceramic 1uF 25V X7R 20% SMD 1206 125C Plastic T/R | C2, C6, C10 | ‎C1206C104K5RAC7800 | 3
Cap | CL31 Series 10 uF 50 V ±10 % Tolerance X5R SMT Multilayer Ceramic Capacitor | C4, C5 | CL31A106KBHNNNE | 2
1uF | Cap Ceramic 1uF 25V X7R 20% SMD 1206 125C Plastic T/R | C8, C11 | CL31B105KBHNFNE | 2
EDAC 690-005-299-043 | Conn Mini Usb Rcpt Ra Type b Smd | J1 | 690-005-299-043 | 1
On Shore Technology OSTTA020161 | Connector Terminal Blocks 2 Position 5mm Solder Straight Thru-Hole 16A | J2, J3, J4, J5, J6, J7, VIN (1 | OSTTA020161 | 7
Molex 504077-1891 | 1.28mm Height Push-Pull microSD Card Socket, SMT, 8 circuits, Lead-Free with Detection Switch | J8 | ‎5040771891‎ | 1
FCI 54602-908LF | Conn Modular Jack F 8 POS 2.54mm Solder RA Thru-Hole 8 Terminal 1 Port Box Cat 3 | J9, J10, J11, J12, J13, J14 | 54602-908LF | 6
Espressif Systems ESP32-WROOM-32 | Wi-Fi/BT BLE Module ESP32-D0WDQ6, SPI Flash, UART | M1 | ‎ESP32-WROOM-32E (8MB)‎ | 1
MBT2222ADW1T1G | General Purpose Transistor, NPN Silicon, 6-Pin SOT-363, Pb-Free, Tape and Reel | Q1 | MBT2222ADW1T1G | 1
Panasonic ERJ-6GEYJ822V | Thick Film Resistors - SMD 0805 8.2Kohms 5% Tol | R1, R2, R3, R4, R5, R6, R7, R8, R9, R10, R11, R12, R13, R14, R15, R16 | ERJ-6GEYJ822V | 16
Vishay Dale CRCW120622K1FKEA | RES SMD 22.1K OHM 1% 1/4W 1206 | R17 | CRCW120622K1FKEA | 1
47.5K | Res Thick Film 1206 47.5K Ohm 1% 0.25W(1/4W) ±100ppm/C Pad SMD Automotive T/R | R18 | RMCF1206FT47K5 | 1
Res1 | Res Thick Film 0603 4.7K Ohm 1% 0.1W(1/10W) ±100ppm/C Pad SMD Automotive T/R | R19 | ‎RMCF0603FT4K70‎ | 1
Res1 | Res Thick Film 0603 470 Ohm 5% 0.1W(1/10W) ±100ppm/C Pad SMD Automotive T/R | R20 | ‎CRGCQ0603J470R | 1
Res1 | Res Thick Film 1.6 x 0.8 mm 150 Ohm 1% 0.1W(1/10W) 100ppm/ C Molded SMD Paper T/R | R21 | RC0603FR-07150RL | 1
TE Connectivity FSM4JH | Switch Tactile OFF (ON) Round Button PC Pins 0.05A 12VDC 1.57N Thru-Hole Radial Tape | S1, S2 | ‎1825910-6 | 2
Texas Instruments (TI) LM1117MPX-ADJ/NOPB | LDO Regulator Pos 1.25V to 13.8V 0.8A 4-Pin(3+Tab) SOT-223 T/R | U1 | LM1117MPX-ADJ/NOPB | 1
Texas Instruments LMZM23601V5SILR | 36-V, 1-A Step-Down DC-DC Power Module in 3.8-mm × 3-mm Package 10-uSiP -40 to 125 | U2 | ‎LMZM23601V5SILR | 1
Texas Instruments SN74AHCT595D | Shift Register Single 8-Bit Serial to Serial/Parallel 16-Pin SOIC Tube | U3, U4, U5 | SN74AHCT595D | 3
CP2102N-A01-GQFN28 | Full Speed USB to UART Bridge USB 2.0 3.3V T/R Automotive 28-Pin QFN EP | U6 | CP2102N-A02-GQFN28R | 1
MBR0520LT1G | Rectifier, Schottky Power; Plastic Sod-123; 0.5 a @ +90c If; +125; 20v; 1000 | VD1, VD2 | SBR80520LT1G | 2

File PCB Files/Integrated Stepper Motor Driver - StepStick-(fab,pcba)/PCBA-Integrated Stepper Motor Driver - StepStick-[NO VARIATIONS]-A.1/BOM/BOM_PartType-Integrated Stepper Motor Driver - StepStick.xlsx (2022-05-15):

Comment | Description | Designator | Footprint | LibRef | Quantity
Lite-On LTST-C193TBKT-5A | Blue 1.6 x 0.8 mm (0603) 130 º Intensity Min 11.2 mcd Typical 15 mcd SMT LED | 5V, 24V | PCB-0603-BoxOverlay | CMP-abba620d38e3747d-7 | 2
KEMET C0805C104K5RACTU | Cap Ceramic 0.1uF 50V X7R 10% SMD 0805 125C Plastic T/R | 2012_0.1u | PCB-m0kg6dhldpqif5mvr6zw-1 | CMP-8264279-17 | 1
AGEO RC0805JR-072KL | RC Series 0805 0.125 W 2 kOhms 5% ±100 ppm/°C SMT Thick Film Chip Resistor | 2012_13.7kR, 2012_100kR | PCB-87ovetinf55hg9zqhv8p-1 | CMP-1854011-4 | 2
Cap | CL31 Series 10 uF 50 V ±10 % Tolerance X5R SMT Multilayer Ceramic Capacitor | 3216_10u1, 3216_10u2, C9 | High Density | CMP-bac072e4006c6507-6 | 3
100nF | CL10 Series 0.1 uF 50 V ±5 % Tolerance X7R SMT Multilayer Ceramic Capacitor | C10 | CAPC1608X09N | CMP-7555619-5 | 1
FCI 54602-908LF | Conn Modular Jack F 8 POS 2.54mm Solder RA Thru-Hole 8 Terminal 1 Port Box Cat 3 | J1 | PCB-kyusfhn5h9rxu8er00w0-1 | CMP-1a15d1442034c5d2-8 | 1
Amphenol ICC 54601-906WPLF | Conn Modular Jack RCP 6 POS 2.54mm Solder RA Thru-Hole 6 Terminal 1 Port Cat 3 Box | J2 | PCBComponent | CMP-bed072b8fb136117-3 | 1
On Shore Technology OSTTE040161 | Connector Terminal Block 4 Position..138" /3.5Mm Space Th Top Screw | J3 | OSTTE040161 | CMP-b52b7c252a8f6aec-1 | 1
Samsung CIGW252010EH4R7MNE | Fixed Ind 4.7UH 1.4A 150MOHM | L2 | PCB-07q76at8oyn5vj86m7fq-1 | CMP-b2fc7f28c15a6d3b-1 | 1
20K | Res Thick Film 1.6 x 0.8 mm 20K Ohm 1% 0.1W(1/10W) 100ppm/ C Molded SMD Paper T/R | R7, R8, R9 | PCB-1ci9j4ma2hnf2m9akcl3-1 | CMP-aa1d6305ca5475da-8 | 3
Res1 | Res Thick Film 0603 4.7K Ohm 1% 0.1W(1/10W) ±100ppm/C Pad SMD Automotive T/R | R19 | PCB-g8ucq7vw1s2sdhfr4zem-1 | CMP-011ec9310fadded9-4 | 1
Res1 | Res Thick Film 0603 470 Ohm 5% 0.1W(1/10W) ±100ppm/C Pad SMD Automotive T/R | R20 | RESC1609X55X30ML10T20 | CMP-120ade6ce4e1cdcd-1 | 1
TE Connectivity 1825057-3 | Switch DIP ON OFF SPST 3 Flush Slide 0.1A 20VDC Gull Wing 2000Cycles 2.54mm SMD T/R | SW1 | PCB-chfgz6m5i36qrmmne85a-1 | CMP-3f99f6ac8d38e05e-1 | 1
AS5047P | AS5047P Series 5.5 V 14-bit On-Axis Magnetic Rotary Position Sensor - TSSOP-14 | U1 | PCB-bn9a8dt4cg24clnvvkgl-1 | CMP-d38a190911520c4d-1 | 1
Trinamic TMC2208 SILENTSTEPSTICK | Step / Direction Driver Board with TMC2209 | U2 | PCB-mklgro9ndndi6uycvhjn-1 | CMP-4859874e3259979e-1 | 1
Texas Instruments PLMR51420XDDCT | SIMPLE SWITCHER® power converter 4.5-V to 36-V, 2-A, synchronous buck with 40-µA IQ 6-SOT-23-THIN -40 to 125 | U4 | PCB-1484289-1 | CMP-ae6e6037501671a9-1 | 1
MBR0520LT1G | Rectifier, Schottky Power; Plastic Sod-123; 0.5 a @ +90c If; +125; 20v; 1000 | VD1, VD2 | SOD-123_B | CMP-3786467-11 | 2

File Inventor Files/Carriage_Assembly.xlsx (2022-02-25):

Item | Part Number | Thumbnail | QTY | Stock Number | Description | REV
1 | 20-2040_150mm |  | 1
2 | 14056_m |  | 4 |  | 14056, 14051, 14053, 14052, 14054_m-2 Hole Inside Corner Brackets
3 | Buffer |  | 2
4 | Carriage_Horizontal_Spacer |  | 2
5 | 20-2040_400mm |  | 1
6 | hex spacer standoff nut M5 L30 |  | 4 |  | STEP AP203 | ANYUNSPECIFIED
7 | Buffer_L |  | 2
8 | Bolt M5 10mm |  | 36
9 | DIN 508, T-Slot Nut M5 |  | 40
10 | 20-2040_300mm |  | 2
11 | 5537T425_T-SLOTTED FRAMING |  | 2 |  | STEP AP203 | ANY
12 | X_CarriageFWD_V2_1 |  | 2
13 | X_CarriageFWDBearing_V2_1_Short |  | 2
14 | X_CarriageBWD_V2_0 |  | 2
15 | Bolt M5 12mm |  | 4

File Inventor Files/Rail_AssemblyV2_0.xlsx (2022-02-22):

Item | Part Number | Thumbnail | BOM Structure | Unit QTY | QTY | Stock Number | Description | REV
1 | 23HS8430B |  | Normal | Each | 1
2 | 2804S_NEMA2115_1Gearbox |  | Normal | Each | 1
3 | Main |  | Normal | Each | 1 |  | Open CASCADE Model
4 | 20-4040_2m |  | Normal | Each | 1
5 | NEMA23_Shroud |  | Normal | Each | 1
6 | 98952A059_ALUM MALE-FEM THRDED HEX STANDOFF |  | Normal | Each | 8 |  | STEP AP203 | ANY
7 | 95783A039_NYLON 6-6 MALE-FEM THRDED HEX STANDOFF |  | Normal | Each | 4 |  | STEP AP203 | ANY
8 | HFS5-4060-2125 |  | Purchased | Each | 1 |  | HFS5-2060, HFS5-2080, HFS5-4060, HFS5-4080, NFS5-2060, NFS5-2080, NFS5-4060, NFS5-4080-HFS5 Series Aluminum Extrusions 20mm Square -3 or more slots-
9 | Integrated_Stepper_NEMA23_Mount |  | Normal | Each | 1
10 | 20-2568_d |  | Purchased | Each | 1 |  | 20-2565, 20-2070, 20-2075, 20-2566, 20-2567, 20-2568, 20-2565-Black, 20-2070-Black, 20-2075-Black, 20-2566-Black, 20-2567-Black, 20-2568-Black_d-20 Series 45 degree support dummy table
11 | 5mm_bore_10mm_width_idlepulley |  | Normal | Each | 1
12 | Tape_Belt_Layer |  | Normal | Each | 1
13 | SDP_sdpsi_a_6a55m028df0912 |  | Normal | Each | 1 |  |  | 10LAST_VERSION
14 | SDP_sdpsi_a_6r25mc1000 |  | Normal | Each | 2 |  |  | 3LAST_VERSION
15 | Carriage_Assembly |  | Normal | Each | 1
16 | NEMA23_StepperonlineMount |  | Normal | Each | 1
17 | 59145_Sensor |  | Normal | Each | 1
18 | RightAngle_SideBracket |  | Normal | Each | 4
19 | Cable_Guide_Holder |  | Normal | Each | 6
20 | RightAngle_PulleySupport |  | Normal | Each | 1
21 | MagnetHolder |  | Normal | Each | 1
22 | MagnetActuatorHolder |  | Normal | Each | 1
23 | 59145_Actuator |  | Normal | Each | 1
24 | Bottom_Foot_Assembly |  | Normal | Each | 3
25 | Bolt M5 8mm |  | Normal | Each | 18
26 | Bolt M5 12mm |  | Normal | Each | 8
27 | Bolt M5 25mm |  | Normal | Each | 1
28 | Bolt M4 10mm |  | Normal | Each | 4
29 | RightAngle_Bracket_60mm |  | Normal | Each | 2
30 | Bolt M5 10mm |  | Normal | Each | 4
31 | DIN 508, T-Slot Nut M5 |  | Normal | Each | 19
32 | Nut M5 |  | Normal | Each | 1

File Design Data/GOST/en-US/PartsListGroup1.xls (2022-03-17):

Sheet: Лист 1
Инв. № подл |  |  |  | Подп. и дата | Взам. инв. № | Инв. № дубл. |  |  | Подп. и дата
Формат | Зона | Поз. | Обозначение |  |  |  | Наименование |  |  |  |  |  | Кол. на исполнение
 |  |  |  |  |  |  |  |  |  |  |  | Лит.
 |  |  |  |  |  |  |  |  |  |  |  | Код
 |  |  |  |  |  |  |  | Изм. | Лист | № докум | Подпись |  | Дата
 |  |  |  |  |  |  |  | Разраб.
 |  |  |  |  |  |  |  | Пров.
 |  |  |  |  |  |  |  | Н.контр
 |  |  |  |  |  |  |  | Утв.
 |  |  |  |  |  |  |  |  |  |  |  |  |  | Копировал

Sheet: Лист 2
Инв. № подл |  |  |  | Подп. и дата | Взам. инв. № | Инв. № дубл. |  |  | Подп. и дата
Формат | Зона | Поз. | Обозначение |  |  |  | Наименование |  |  |  |  | Кол. на исполнение
 |  |  |  |  |  |  |  | Изм. | Лист | № докум. | Подп. | Дата
 |  |  |  |  |  |  |  |  |  |  |  |  | Копировал
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

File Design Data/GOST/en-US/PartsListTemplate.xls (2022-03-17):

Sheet: Лист 1
 | Формат | Зона |  | Поз. |  | Обозначение |  |  |  | Наименование |  |  |  | Кол. | Приме-чание
Подп. и дата
Инв. № дубл.
Взам. инв. №
Подп. и дата
 | Изм. |  | Лист |  | № докум |  | Подпись | Дата
Инв. № подл | Разраб. |  |  |  |  |  |  |  |  |  | Литера |  | Лист |  |  | Листов
 | Пров.
 | Н.контр
 | Утв.
 |  |  |  |  |  |  |  |  | Копировал |  |  | Формат А4

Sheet: Лист 2
 | Формат | Зона |  | Поз. |  | Обозначение |  |  |  | Наименование |  | Кол. | Приме-чание
Подп. и дата
Инв. № дубл.
Взам. инв. №
Подп. и дата
Инв. № подл
 | Изм. |  | Лист |  | № докум. |  | Подп. |  | Дата
 |  |  |  |  |  |  |  | Копировал |  |  | Формат А4
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

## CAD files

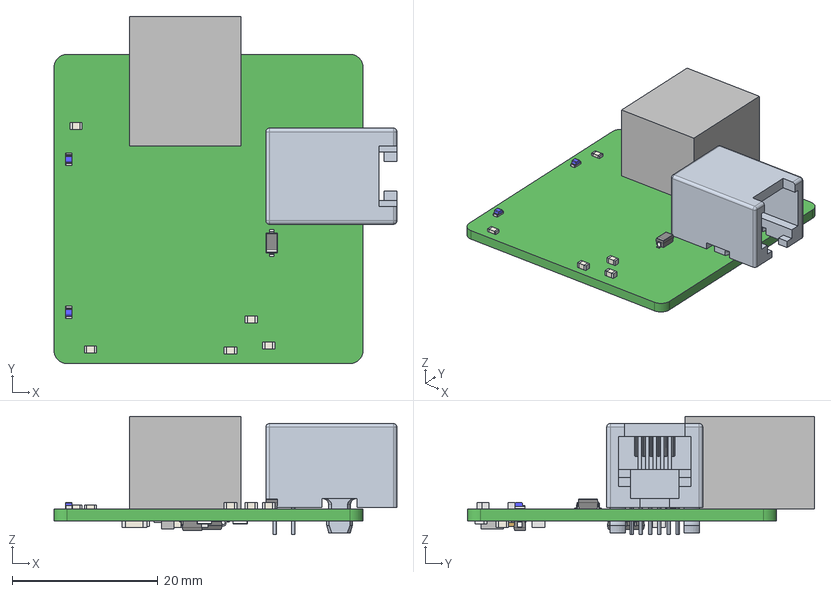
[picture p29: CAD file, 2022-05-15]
PCB Files/Integrated Stepper Motor Driver - StepStick-(fab,pcba)/FAB-Integrated Stepper Motor Driver - StepStick-A.1/ExportSTEP/Main.step
47.0 x 47.6 x 16.2 mm
Extruded x 39
0805_Resistor x 2
User_Library-LTST-C190TBKT_Pad x 2
User_Library-LTST-C190TBKT_Pad005 x 2
User_Library-LTST-C190TBKT_Pad001 x 2
User_Library-LTST-C190TBKT_Pad004 x 2
User_Library-LTST-C190TBKT_Pad003 x 2
User_Library-LTST-C190TBKT_Lens x 2
tssop14-2
54601-906WPLFc
SOD-123 x 2

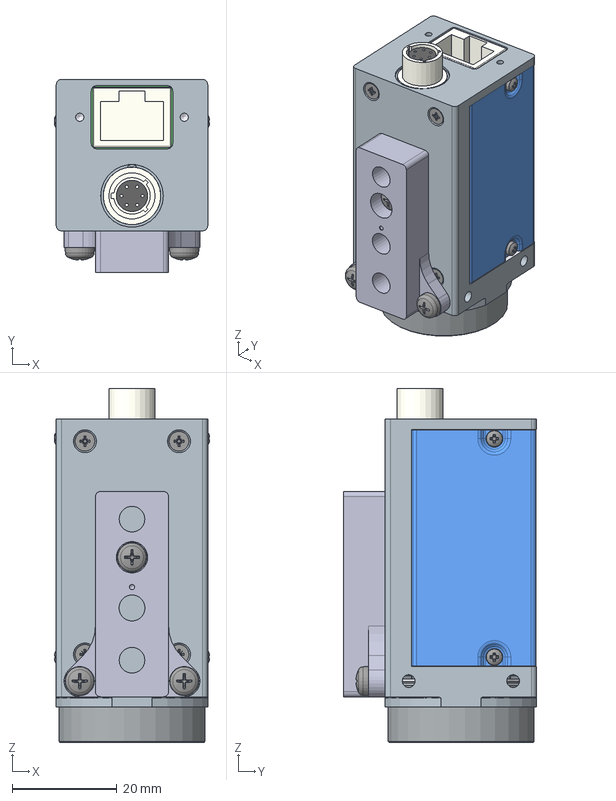
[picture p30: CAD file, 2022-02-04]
Inventor Files/121-11-22/121-11-22(FPGA-RJ45_C-Frontpl-18,1_ER-11,7).stp
29.7 x 37.0 x 67.7 mm
121-11-22(FPGA-RJ45_C-Frontpl-18,1_ER-11,7)Redu
121-11-2-00-02(TripodAdapter)
DIN EN ISO 7045 H M3 x 6 - 4.8 - H x 3

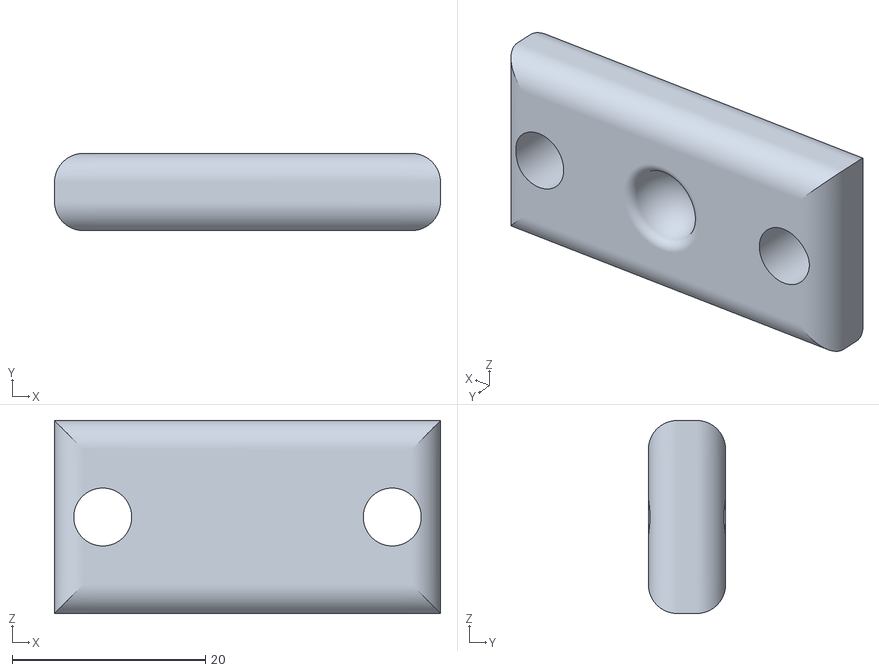
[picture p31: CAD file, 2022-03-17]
Inventor Files/Carriage Updates/TestBearingPad.stl
40.0 x 8.00 x 20.0

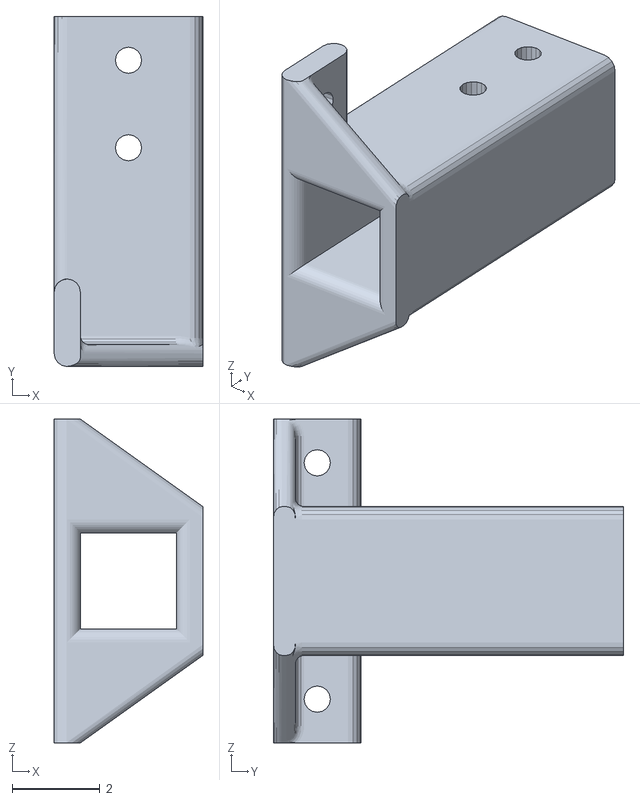
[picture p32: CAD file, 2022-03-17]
Inventor Files/Linear_Extender.stl
3.40 x 8.00 x 7.40

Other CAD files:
Design Data/AIT/Mold Design/mold design stop pin.ipt
Design Data/Cable & Harness/en-US/harness.iam
Design Data/Tube & Pipe/en-US/piping runs.iam
Inventor Files/10mm_Idle_Pulley.ipt
Inventor Files/10mm_Spacer.ipt
Inventor Files/120deg_Tslot_Gusset.ipt
Inventor Files/121-11-22/121-11-2-00-02(TripodAdapter).ipt
Inventor Files/121-11-22/DIN EN ISO 7045 H M3 x 6 - 4.8 - H.ipt
Inventor Files/121-11-22/OldVersions/121-11-22(FPGA-RJ45_C-Frontpl-18,1_ER-11,7).0001.iam
Inventor Files/17mmBeltGuide.ipt
Inventor Files/18mm_Bushing.ipt
Inventor Files/24-vdc-13a-switching-power-supply-meanwell-1.snapshot.2/24 Volt Power Supply 13A MeanWell Amazon.ipt
Inventor Files/3mmSpacer.ipt
Inventor Files/3mm_Spacer.ipt
Inventor Files/4mm_Roller_Spacer.ipt
Inventor Files/4mm_Roller_Spacer_L.ipt
Inventor Files/4mm_Roller_Spacer_R.ipt
Inventor Files/4mm_Roller_Spacer_simple3mm.ipt
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

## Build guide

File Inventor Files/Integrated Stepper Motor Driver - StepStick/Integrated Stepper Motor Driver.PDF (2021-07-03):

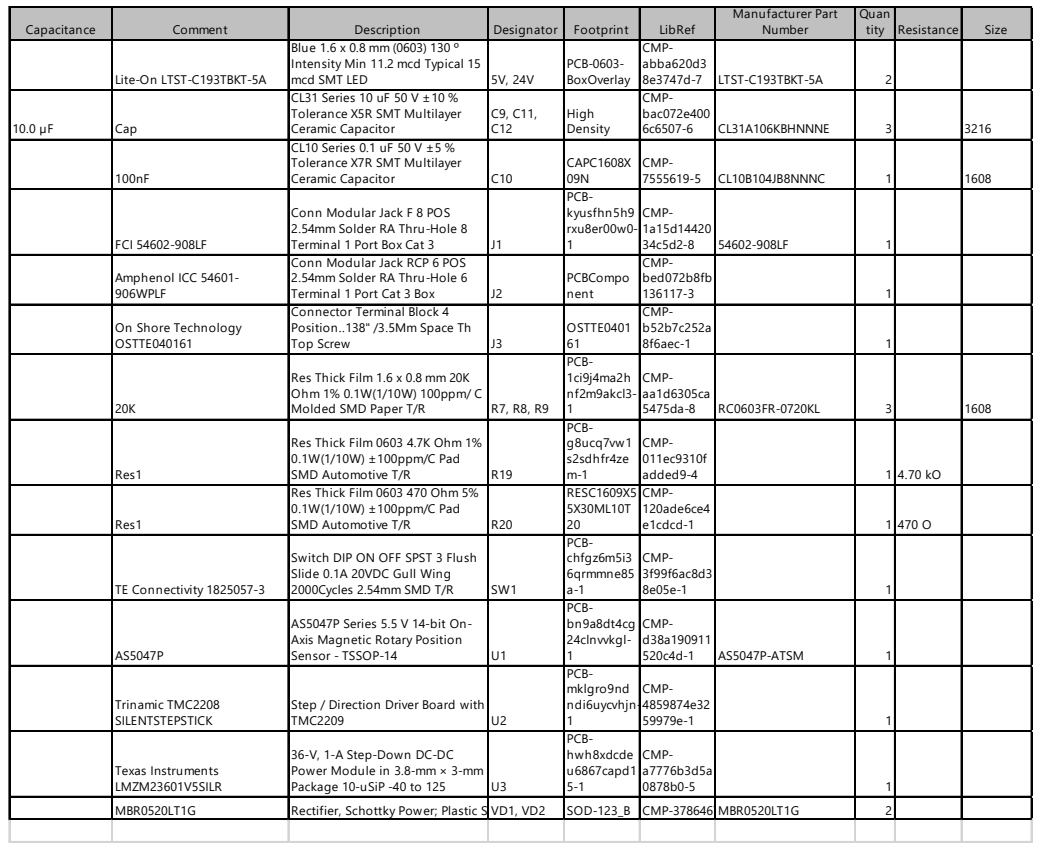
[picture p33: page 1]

Capacitance | Comment | Description | Designator | Footprint | LibRef | Manufacturer Part Number | Quan tity | Resistance | Size

Lite-On LTST-C193TBKT-5A | Blue 1.6 x 0.8 mm (0603) 130 º Intensity Min 11.2 mcd Typical 15 mcd SMT LED | 5V, 24V | PCB-0603-BoxOverlay | CMP-abba620d3 8e3747d-7 | LTST-C193TBKT-5A | 2

10.0 µF | Cap | CL31 Series 10 uF 50 V ±10 % Tolerance X5R SMT Multilayer Ceramic Capacitor | C9, C11, C12 | High Density | CMP-bac072e400 6c6507-6 | CL31A106KBHNNNE | 3 | | 3216

100nF | CL10 Series 0.1 uF 50 V ±5 % Tolerance X7R SMT Multilayer Ceramic Capacitor | C10 | CAPC1608X 09N | CMP-7555619-5 | CL10B104JB8NNNC | 1 | | 1608

FCI 54602-908LF | Conn Modular Jack F 8 POS 2.54mm Solder RA Thru-Hole 8 Terminal 1 Port Box Cat 3 | J1 | PCB-kyusfhn5h9 rxu8er00w0-1 | CMP-1a15d14420 34c5d2-8 | 54602-908LF | 1

Amphenol ICC 54601-906WPLF | Conn Modular Jack RCP 6 POS 2.54mm Solder RA Thru-Hole 6 Terminal 1 Port Cat 3 Box | J2 | PCBCompo nent | CMP-bed072b8fb 136117-3 | | 1

On Shore Technology OSTTE040161 | Connector Terminal Block 4 Position..138" /3.5Mm Space Th Top Screw | J3 | OSTTE0401 61 | CMP-b52b7c252a 8f6aec-1 | | 1

20K | Res Thick Film 1.6 x 0.8 mm 20K Ohm 1% 0.1W(1/10W) 100ppm/ C Molded SMD Paper T/R | R7, R8, R9 | PCB-1ci9j4ma2h nf2m9akcl3-1 | CMP-aa1d6305ca 5475da-8 | RC0603FR-0720KL | 3 | | 1608

Res1 | Res Thick Film 0603 4.7K Ohm 1% 0.1W(1/10W) ±100ppm/C Pad SMD Automotive T/R | R19 | PCB-g8ucq7vw1 s2sdhfr4ze m-1 | CMP-011ec9310f added9-4 | | 1 | 4.70 kO

Res1 | Res Thick Film 0603 470 Ohm 5% 0.1W(1/10W) ±100ppm/C Pad SMD Automotive T/R | R20 | RESC1609X5 5X30ML10T 20 | CMP-120ade6ce4 e1cdcd-1 | | 1 | 470 O

TE Connectivity 1825057-3 | Switch DIP ON OFF SPST 3 Flush Slide 0.1A 20VDC Gull Wing 2000Cycles 2.54mm SMD T/R | SW1 | PCB-chfgz6m5i3 6qrmmne85 a-1 | CMP-3f99f6ac8d3 8e05e-1 | | 1

AS5047P | AS5047P Series 5.5 V 14-bit On-Axis Magnetic Rotary Position Sensor - TSSOP-14 | U1 | PCB-bn9a8dt4cg 24clnvvkgl-1 | CMP-d38a190911 520c4d-1 | AS5047P-ATSM | 1

Trinamic TMC2208 SILENTSTEPSTICK | Step / Direction Driver Board with TMC2209 | U2 | PCB-mklgro9nd ndi6uycvhjn-1 | CMP-4859874e32 59979e-1 | | 1

Texas Instruments LMZM23601V5SILR | 36-V, 1-A Step-Down DC-DC Power Module in 3.8-mm × 3-mm Package 10-uSiP -40 to 125 | U3 | PCB-hwh8xdcde u6867capd1 5-1 | CMP-a7776b3d5a 0878b0-5 | | 1

MBR0520LT1G | Rectifier, Schottky Power; Plastic SoVD, VD 2 | | SO D -123_B | CM P-3786467- MBR0520LT1G | | 2

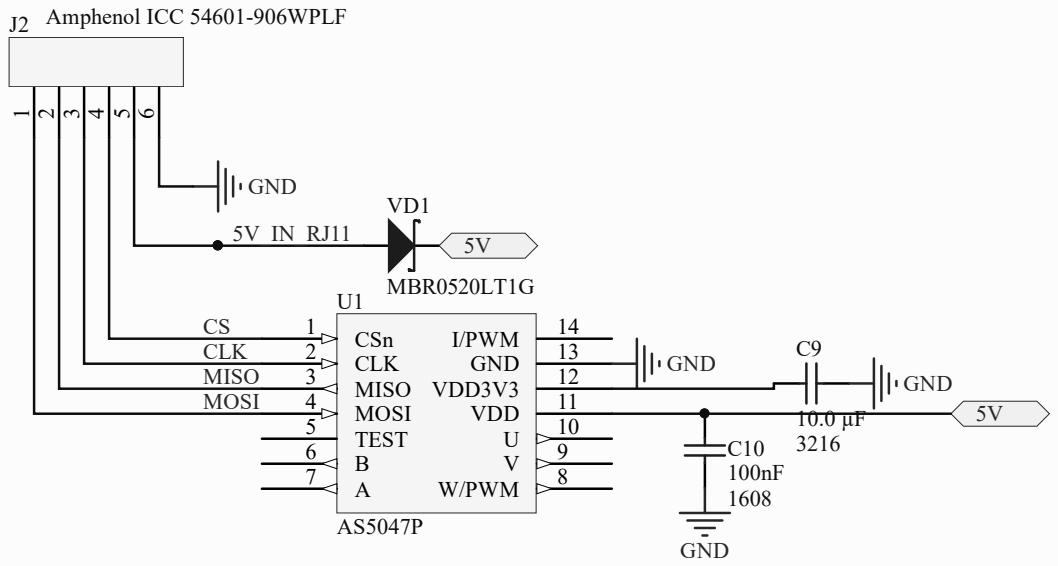
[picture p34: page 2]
Date:; Sheet of; File:; Magnetic_Encoder.SchDoc; Drawn By:; CSn 1 CLK 2 MISO 3 MOSI 4 TEST 5 B 6; W/PWM; 10 VDD; 11 VDD3V3; 12 GND; 13 I/PWM; J2 Amphenol ICC 54601-906WPLF

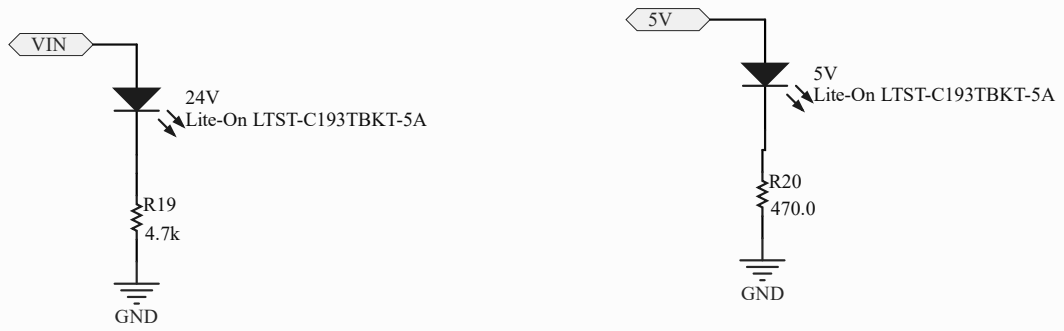
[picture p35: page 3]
24V Lite-On; PI24V02 POVIN

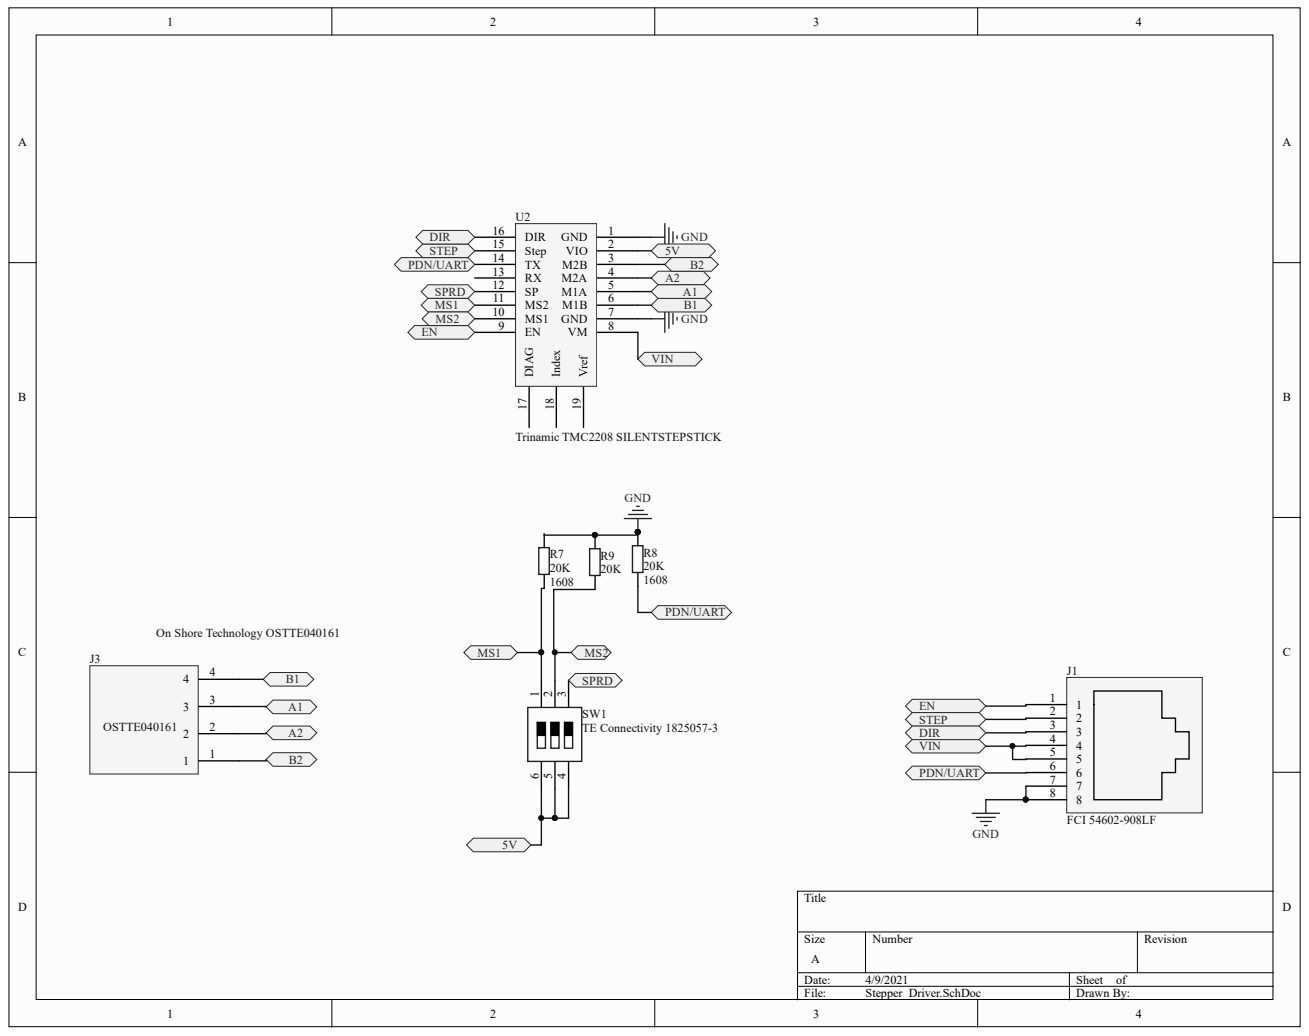
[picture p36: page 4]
Date:; Sheet of; File:; Stepper_Driver.SchDoc; Drawn By:; TE Connectivity 1825057-3; FCI 54602-908LF; DIR 16; 8 GND; 3 VIO; 2 GND; Index 18; Vref 19; Trinamic TMC2208 SILENTSTEPSTICK

On Shore Technology OSTTE040161

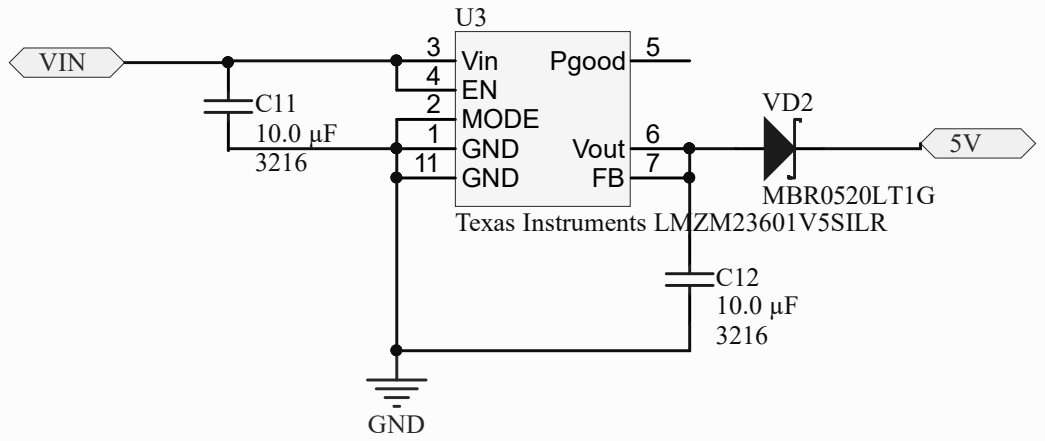
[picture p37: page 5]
s Ins

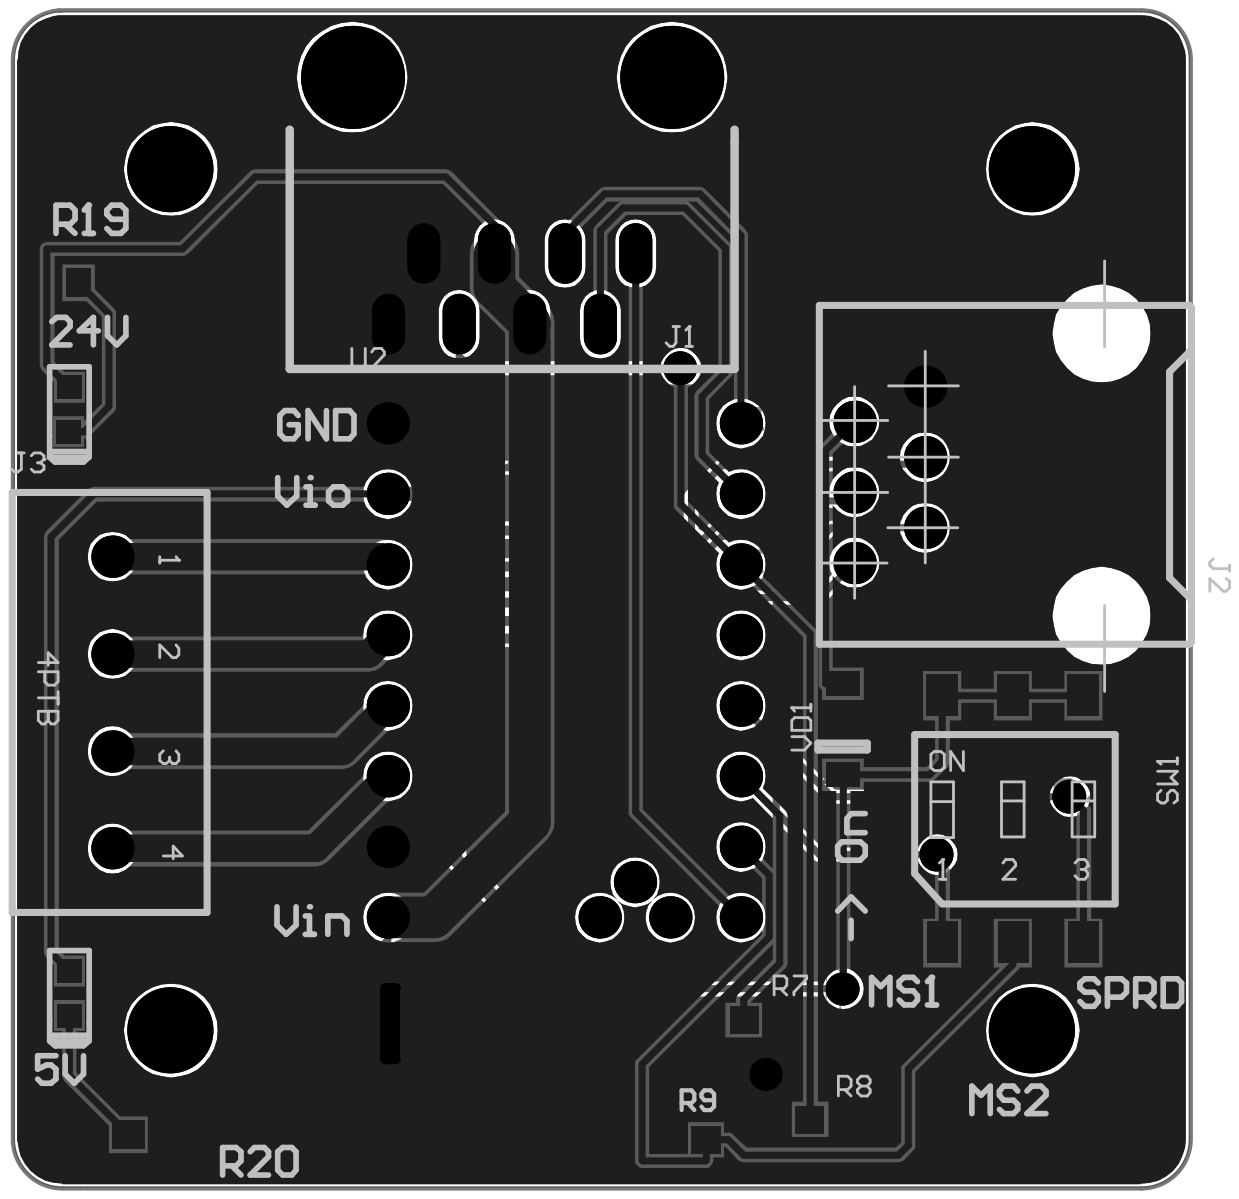
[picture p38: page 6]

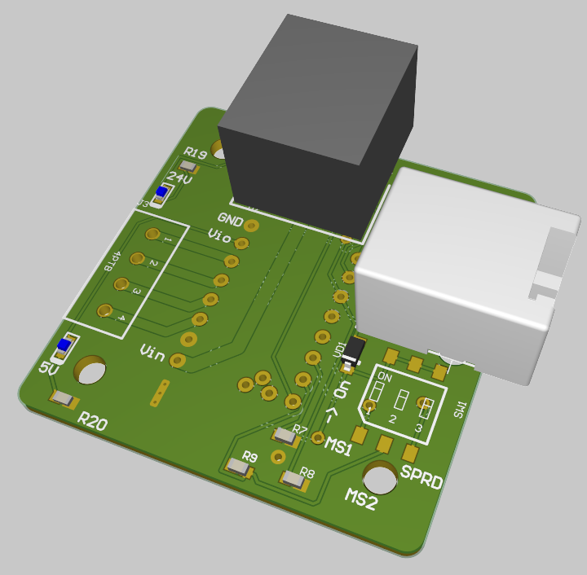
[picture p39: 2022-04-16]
assets/Electrical_assets/IntegratedStepStickDriver.png

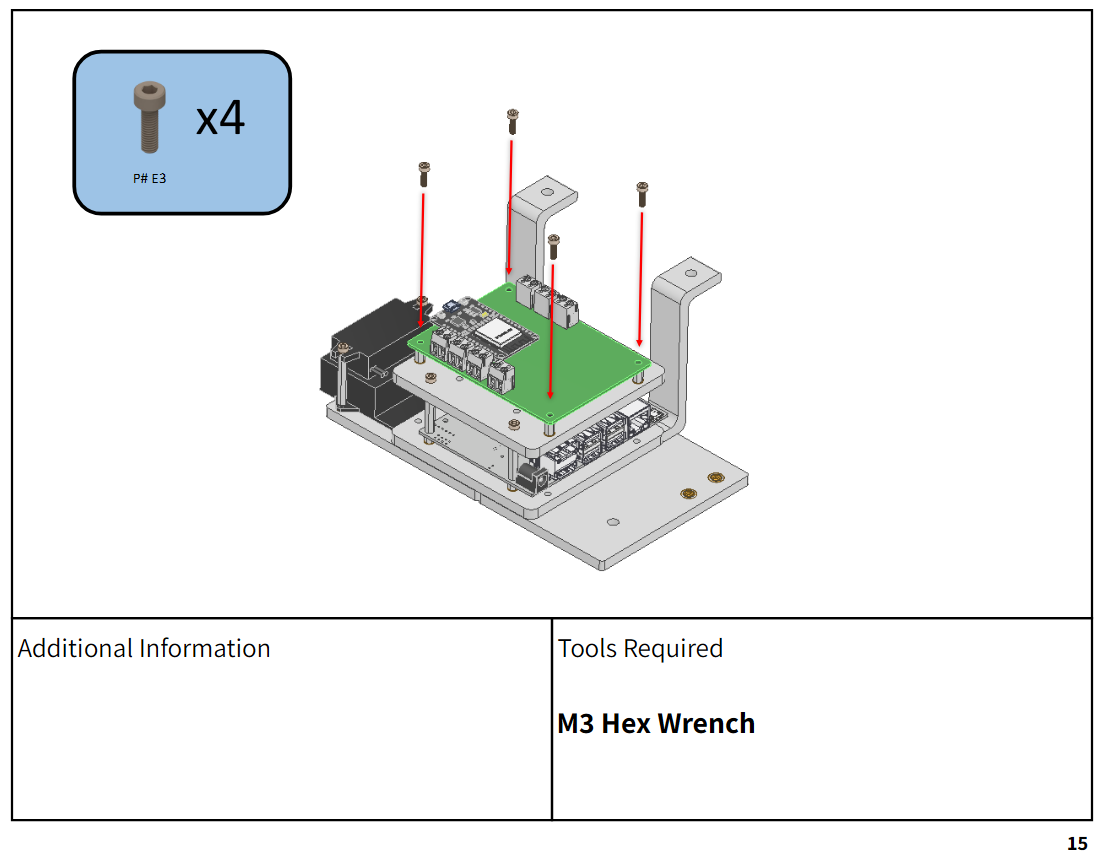
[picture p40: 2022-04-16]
assets/Mechanical_assets/IE_assemblydiagram.png

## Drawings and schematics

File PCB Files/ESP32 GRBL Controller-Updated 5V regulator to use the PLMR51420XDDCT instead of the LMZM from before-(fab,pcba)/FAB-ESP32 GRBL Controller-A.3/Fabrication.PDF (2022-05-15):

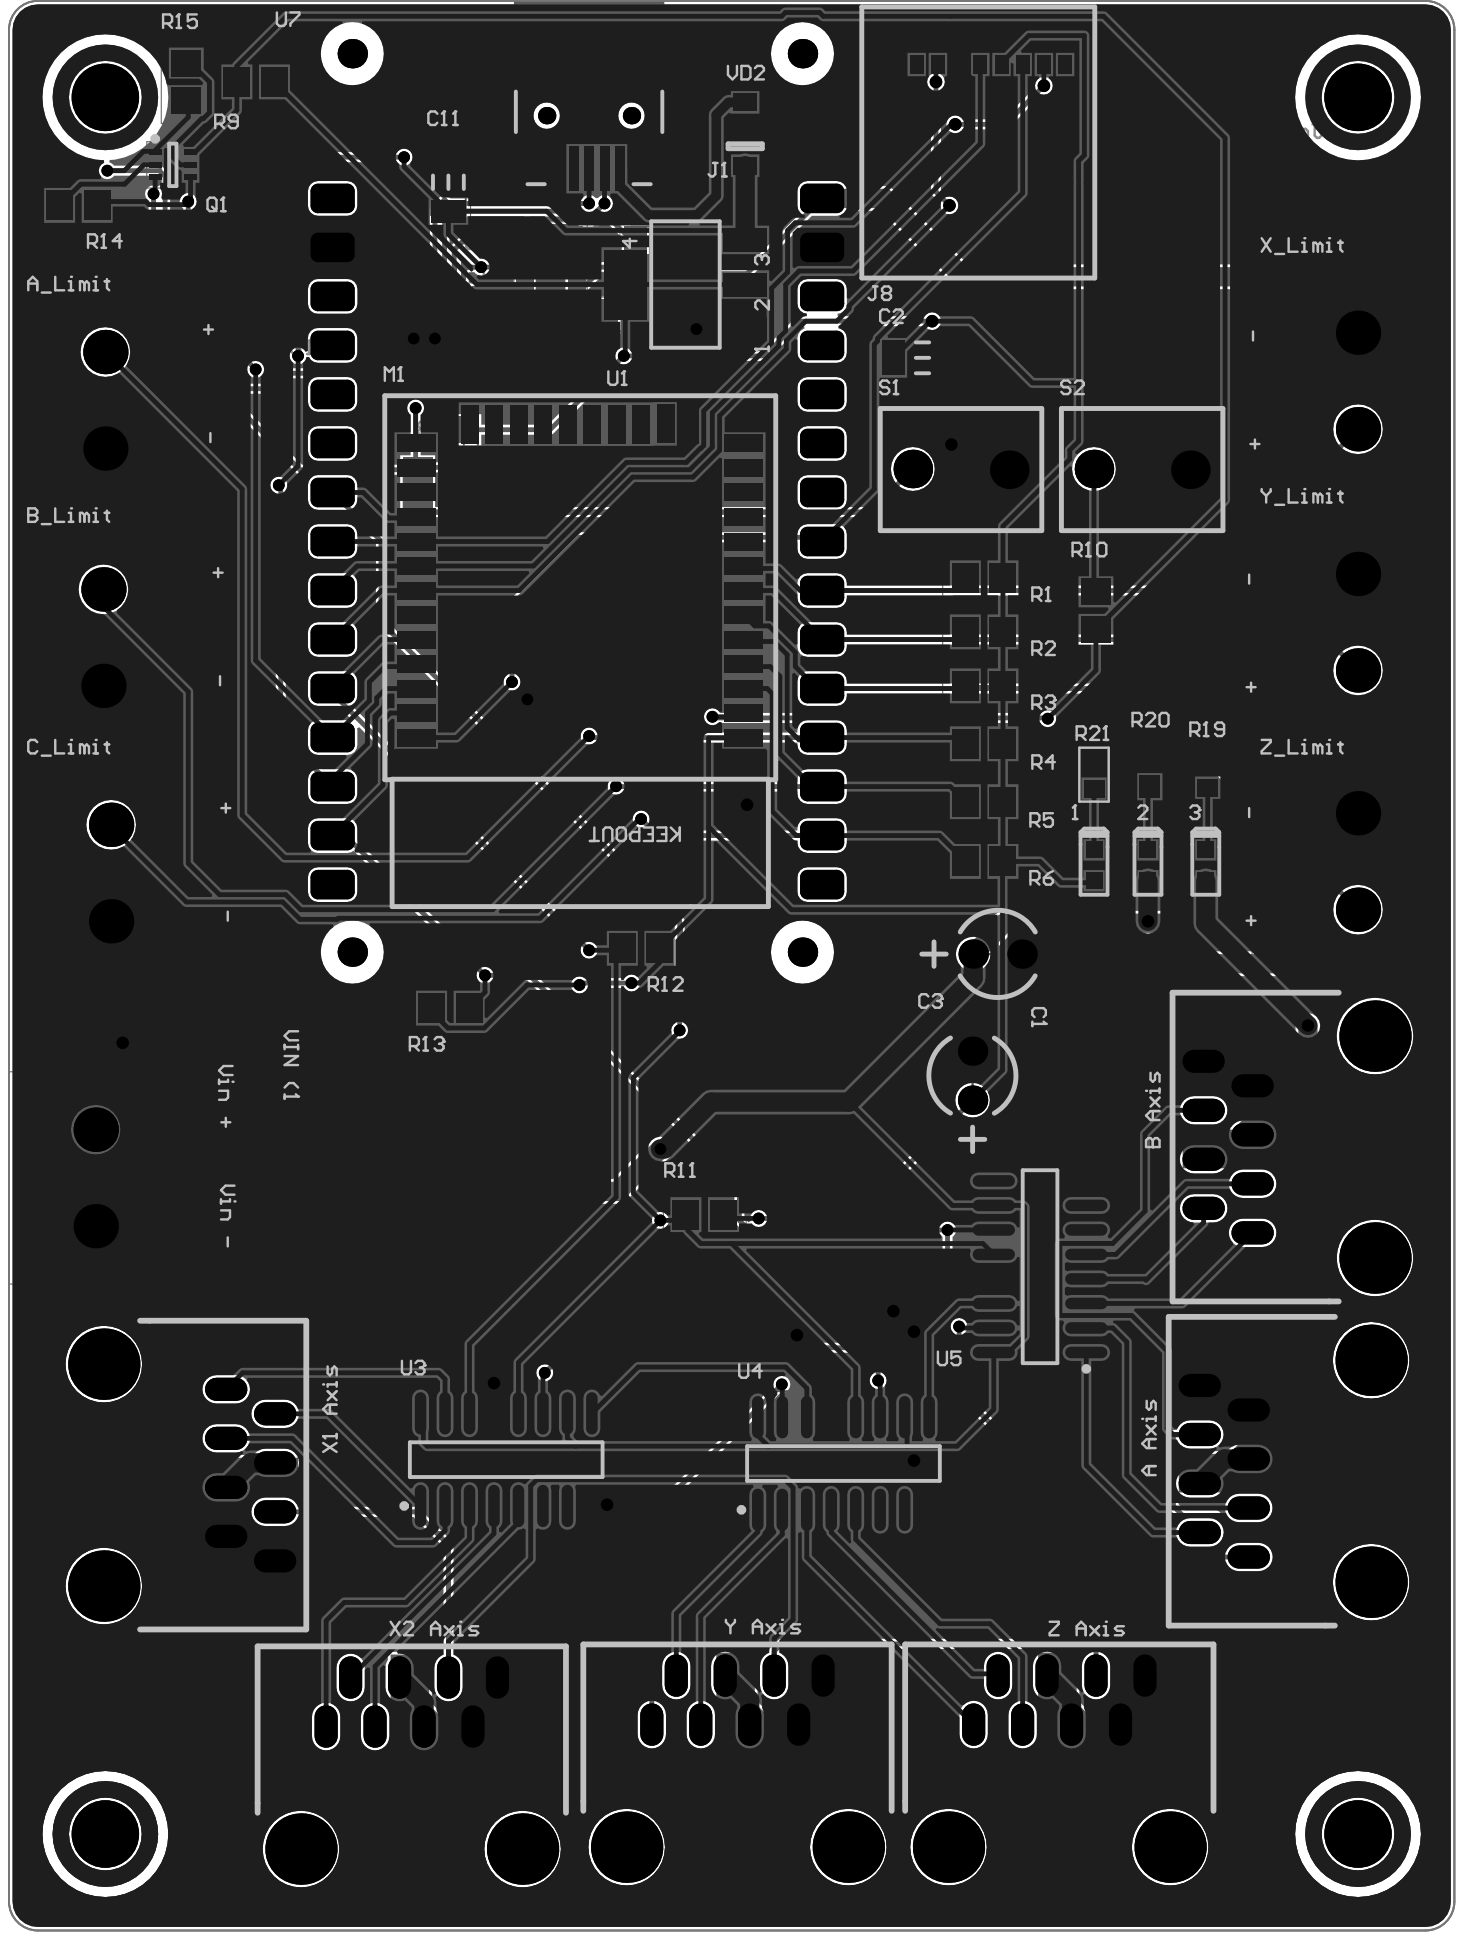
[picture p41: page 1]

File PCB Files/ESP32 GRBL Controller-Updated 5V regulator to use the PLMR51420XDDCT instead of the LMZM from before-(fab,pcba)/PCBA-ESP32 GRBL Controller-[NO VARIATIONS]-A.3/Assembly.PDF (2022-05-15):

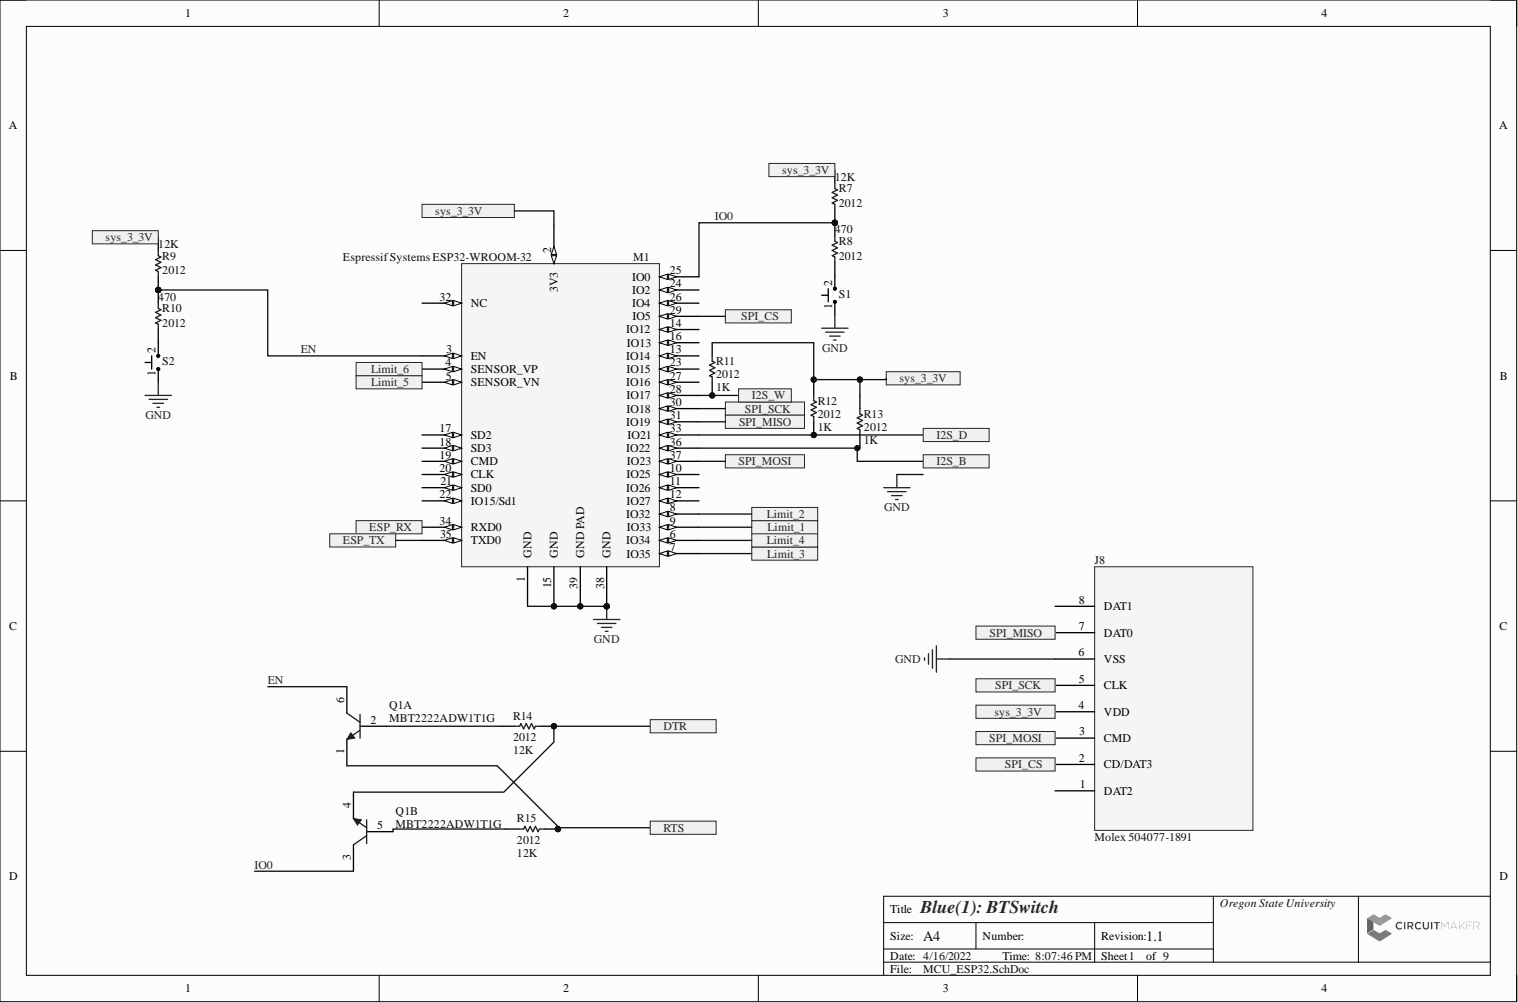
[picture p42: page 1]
Blue(1): BTSwitch; GND 1; GND 15; GND 38; GND PAD 39

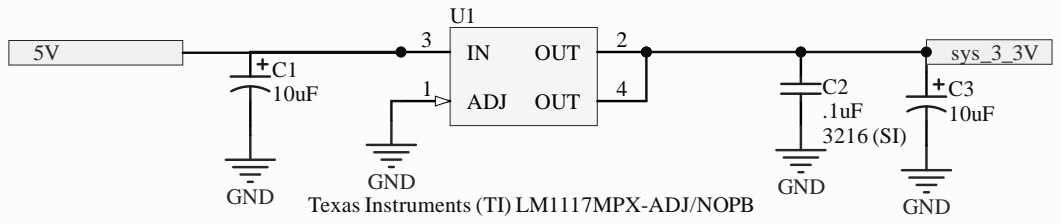
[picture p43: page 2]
Texas In

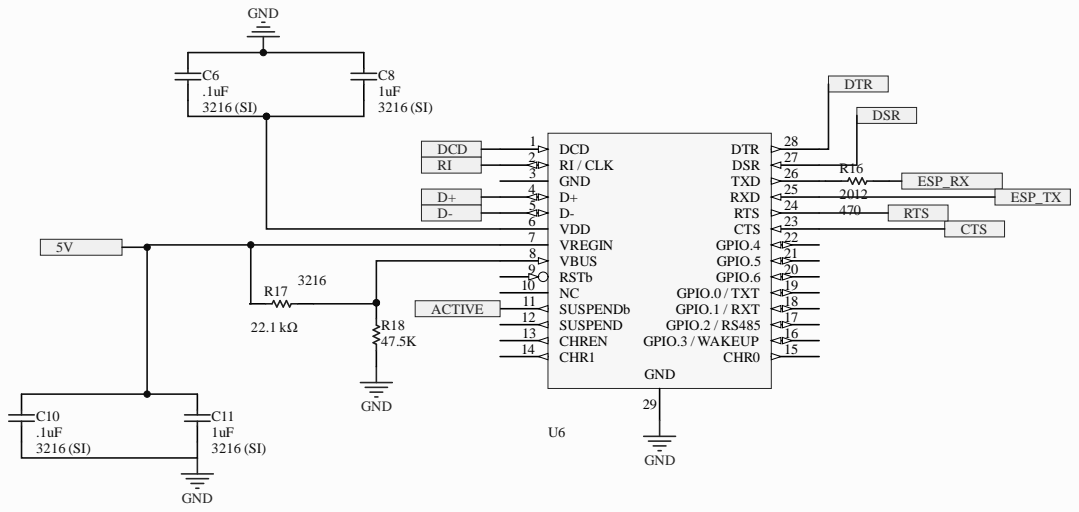
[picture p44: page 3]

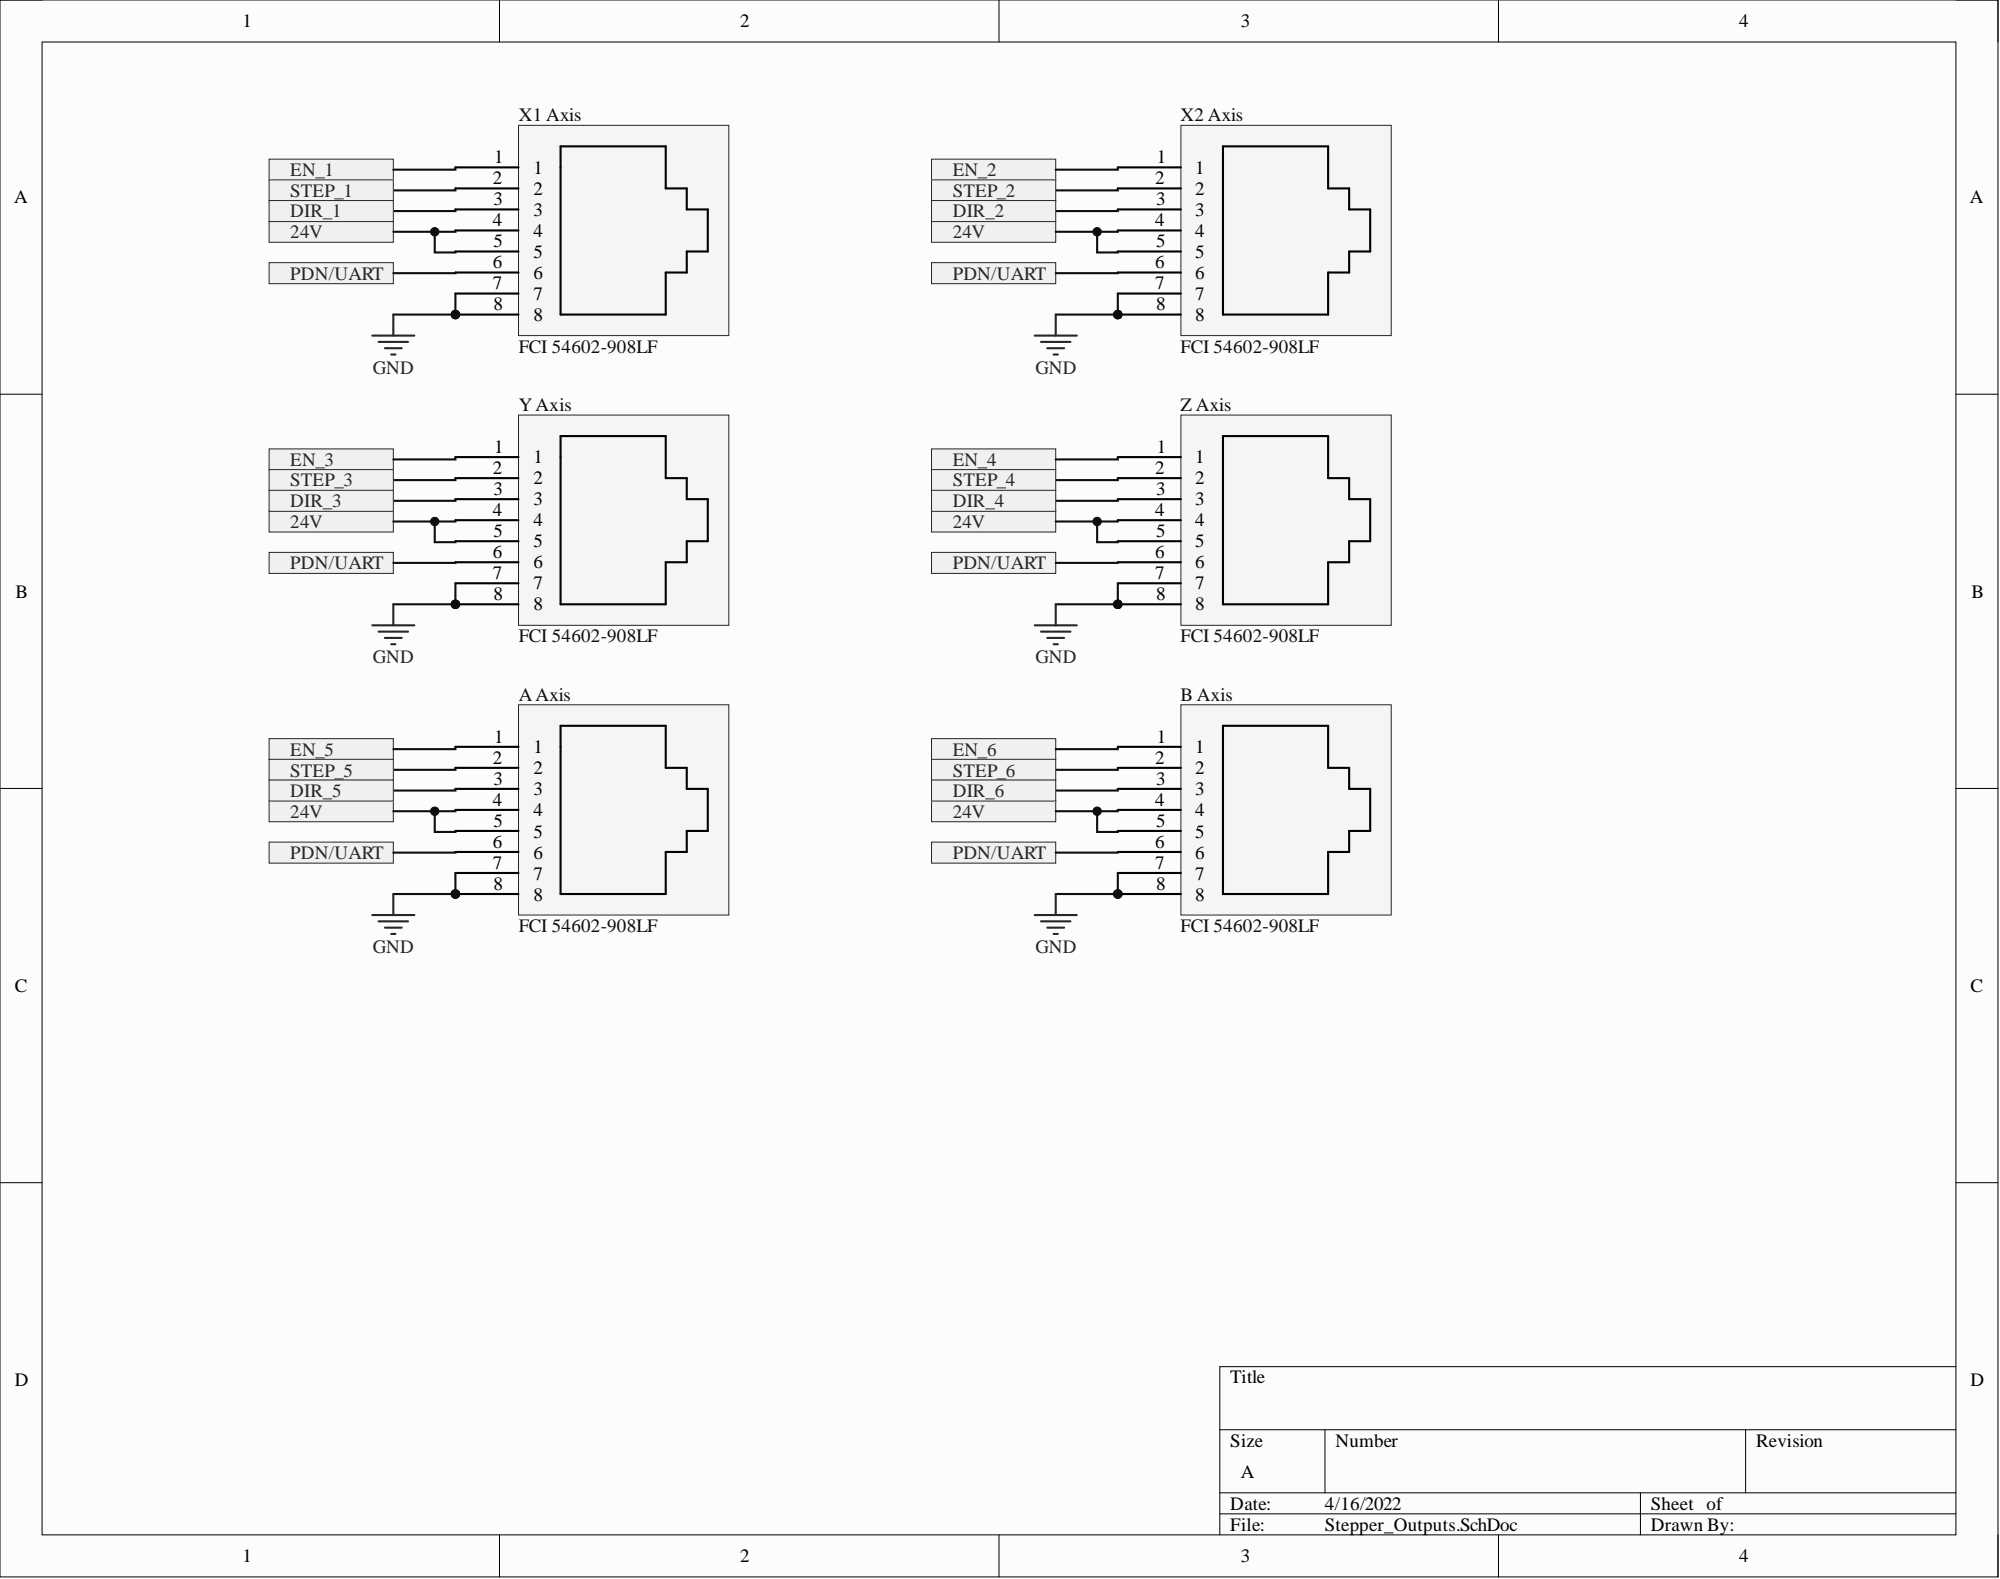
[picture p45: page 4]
File:; Stepper_Outputs.SchDoc; Drawn By:; X1 Axis; FCI 54602-908LF; X2 Axis; Z Axis; Y Axis; A Axis; B Axis; PIA Axis01; PIA Axis02; PIA Axis03; PIA Axis04; PIA Axis05; PIA Axis06; PIA Axis07; PIA Axis08; COA Axis; PIB Axis01; PIB Axis02; PIB Axis03; PIB Axis04; PIB Axis05; PIB Axis06; PIB Axis07; PIB Axis08; COB Axis; PIX1 Axis01; PIX1 Axis02; PIX1 Axis03; PIX1 Axis04; PIX1 Axis05; PIX1 Axis06; PIX1 Axis07; PIX1 Axis08; COX1 Axis; PIX2 Axis01; PIX2 Axis02; PIX2 Axis03; PIX2 Axis04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

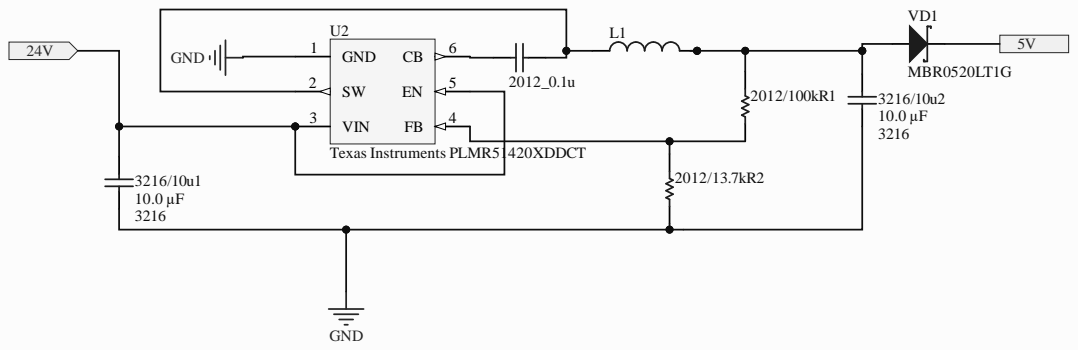
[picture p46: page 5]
Texas In; s PLMR5

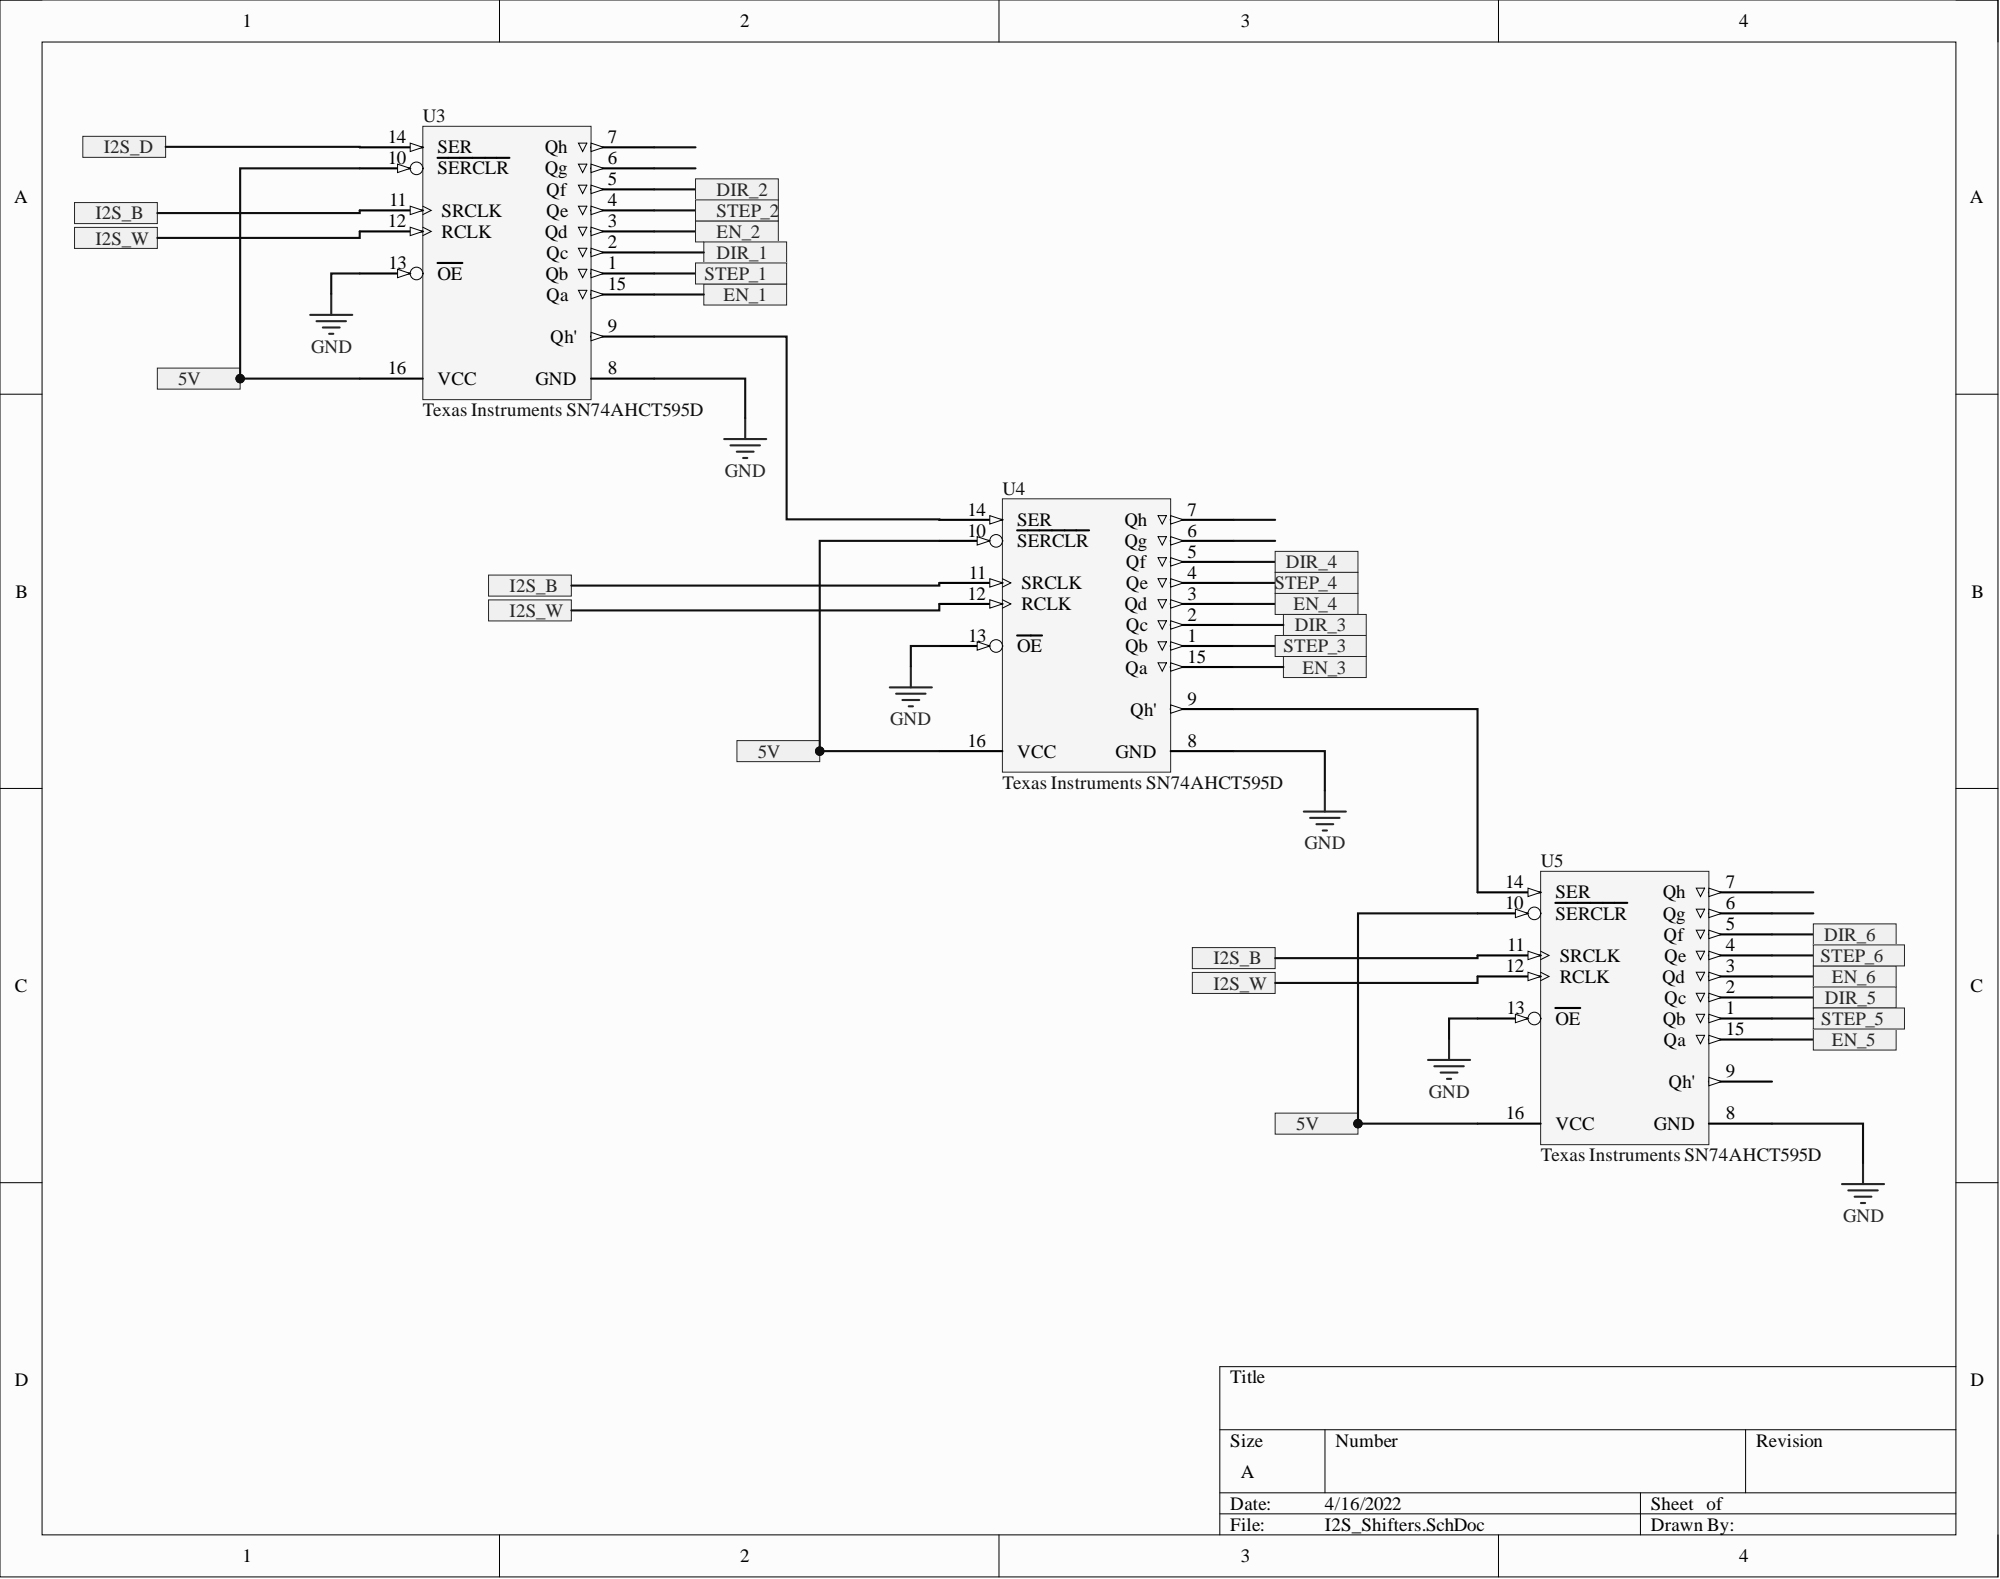
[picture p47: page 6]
File:; I2S_Shifters.SchDoc; Drawn By:; SER 14 SERCLR 10; GND; 8 VCC 16; Texas Instruments SN74AHCT595D; SER 14; RCLK 12; SERCLR 10

PIU3011 | SRCLK 11
PIU3012 | | RCLK 12 PIU303

POI2S0W POI2S0W I2S_W | | | PIU3013 | OE 13 | POEN02 EN_2

PIU4011 | SRCLK 11

I2S_W | | | OE 13 | POEN04 EN_4

SERCLR 10

PIU5011 | SRCLK 11

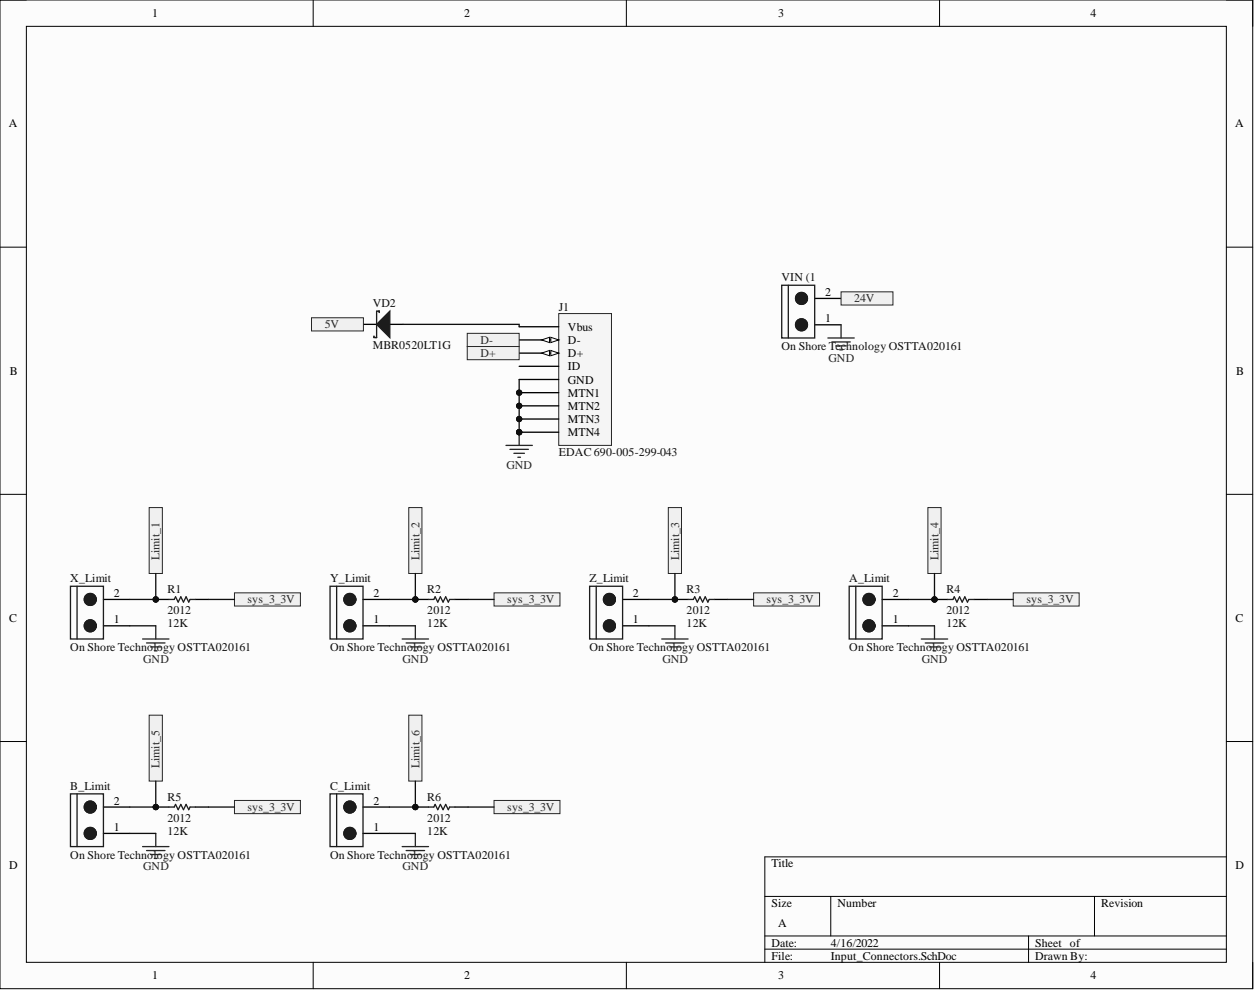
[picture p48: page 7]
File:; Input_Connectors.SchDoc; Drawn By:; EDAC 690-005-299-043; VIN (1

On Shore Technology OSTTA020161

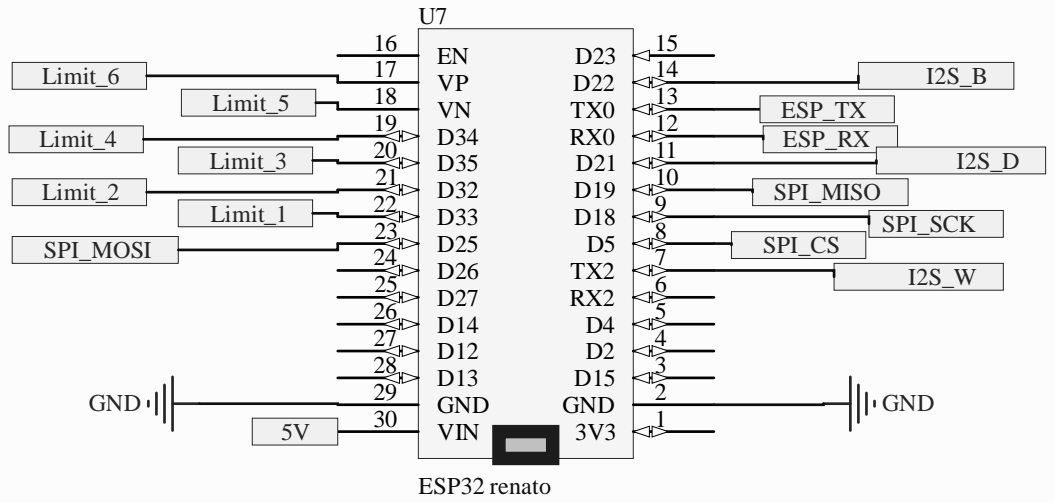
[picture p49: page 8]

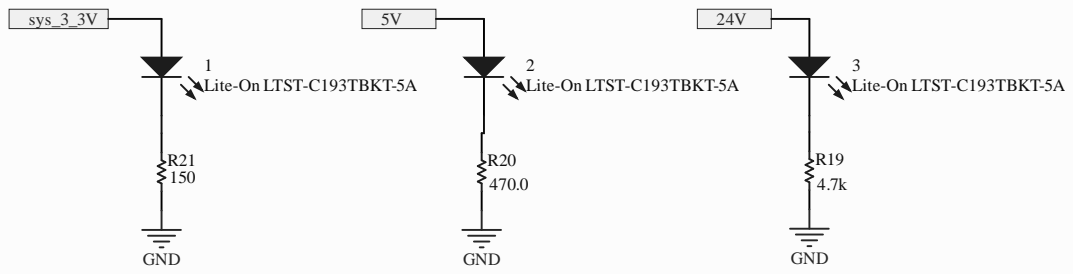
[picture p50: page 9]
PIR1902 COR19; PI102 POsys0303V

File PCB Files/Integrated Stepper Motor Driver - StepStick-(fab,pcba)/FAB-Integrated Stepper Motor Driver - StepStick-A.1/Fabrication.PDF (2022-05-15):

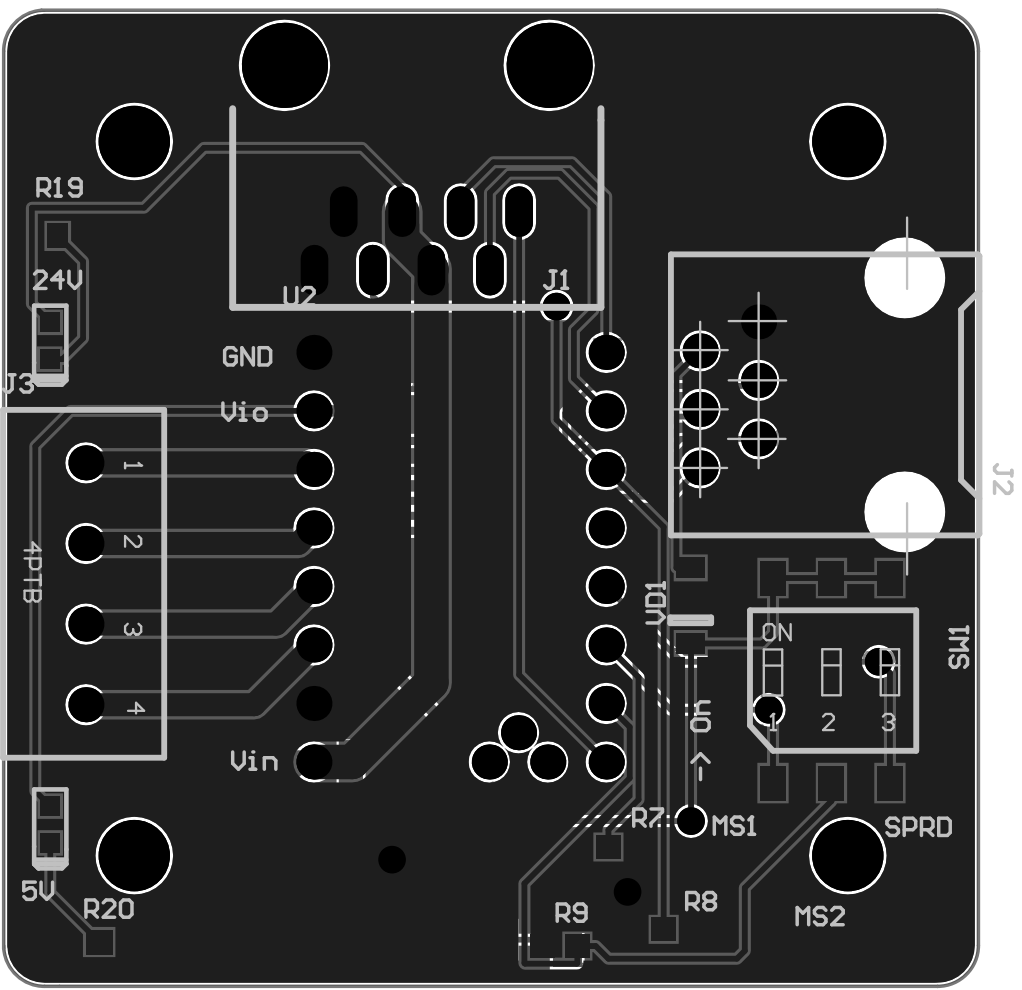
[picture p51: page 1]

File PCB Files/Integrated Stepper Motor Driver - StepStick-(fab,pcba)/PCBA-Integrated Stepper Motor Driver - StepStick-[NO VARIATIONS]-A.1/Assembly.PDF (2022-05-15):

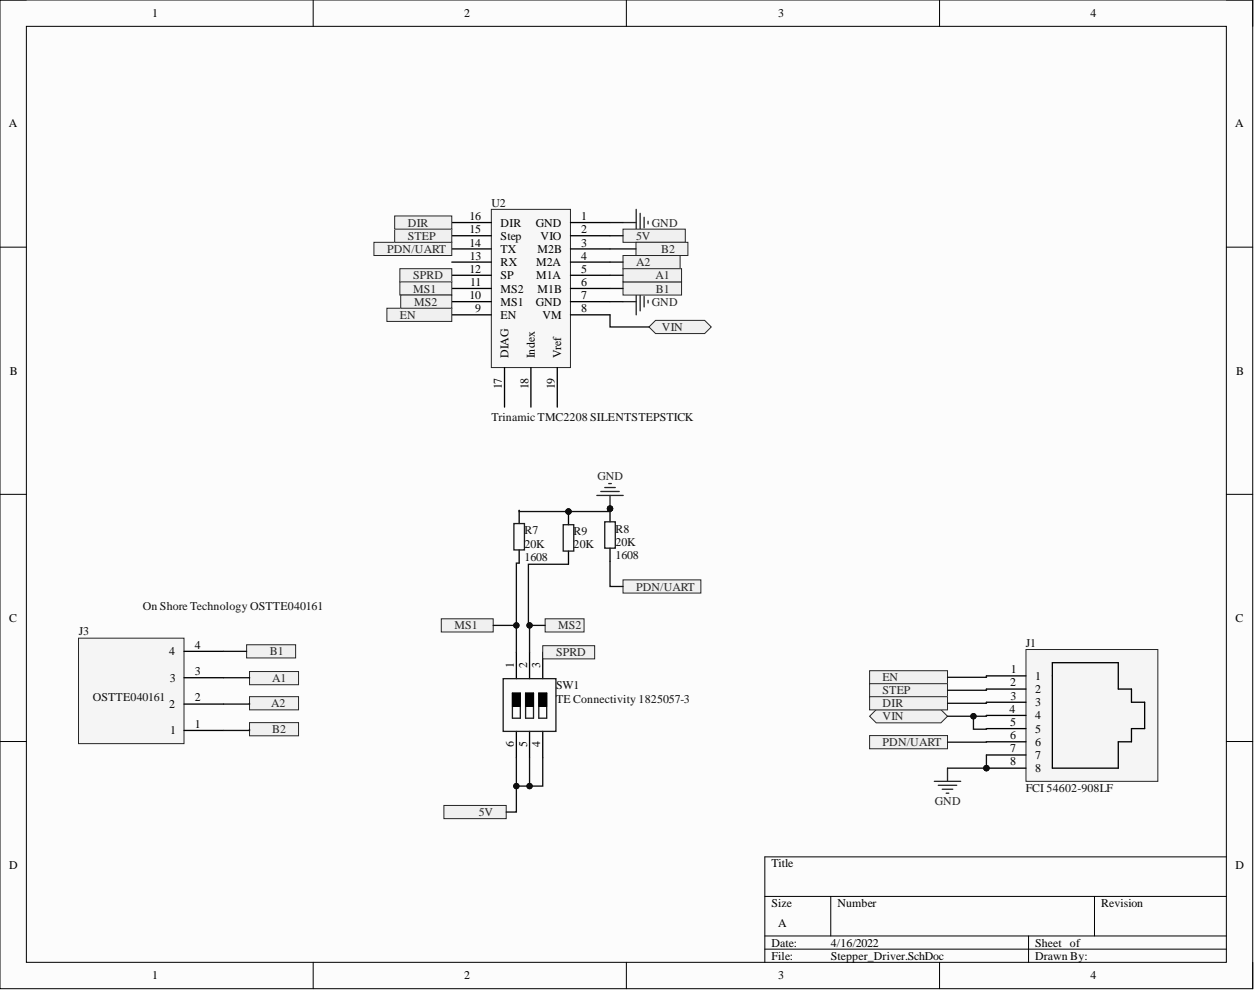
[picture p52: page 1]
Date:; Sheet of; File:; Stepper_Driver.SchDoc; Drawn By:; TE Connectivity 1825057-3; FCI 54602-908LF; DIR 16 Step 15 TX 14 RX 13 SP 12 MS2 11 MS1 10; 8 GND; 3 VIO; 2 GND; DIAG 17; Index 18; Vref 19; Trinamic TMC2208 SILENTSTEPSTICK

On Shore Technology OSTTE040161

Date:; Sheet of; File:; Magnetic_Encoder.SchDoc; Drawn By:; CSn 1 CLK 2 MISO 3 MOSI 4 TEST 5 B 6; W/PWM; 10 VDD; 11 VDD3V3; 12 GND; 13 I/PWM; J2 Amphenol ICC 54601-906WPLF

Texas In; s PLMR5

PIR1902 COR19; PIR2002 COR20; PI24V02 POVIN

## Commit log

2021-07-03 create new repo for hyperrail
    [1.iam, 11mm_BearingWheel.0002.ipt, 11mm_BearingWheel.ipt, 120deg_Tslot_Gusset.0005.ipt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]
2021-07-03 Branch to contain a stripped version of the project This branch only contains code for a cleaner environment.
    [1.iam, 11mm_BearingWheel.0002.ipt, 11mm_BearingWheel.ipt, 120deg_Tslot_Gusset.0005.ipt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]
2021-07-07 Laid out basic service backing for talking over serial to the ESP32
2021-07-07 Added basic functionality for the ESP32 driver
2021-07-12 Added parsing of realtime status to pull position. Publishing both the work position and machine position to the "current_position" topic
2021-07-12 Added ESP32 command output docs
2021-07-12 Subscribe to an empty topic 'gcode_feeder' This topic takes given strings and passes them along to the ESP32 where they are interpreted as gcode
2021-07-17 Started working on sensor package. Currently trying to figure out writing a library to house all sensor information in an abstracted class
2021-07-26 Deleted eGreenhouse sensor package as that should be its own branch
2021-08-20 Created library for conducting basic sensor reads on a K30 CO2 sensor.
2021-08-21 Added adafruit libraries locally to ensure continuity. Basic test bench for using all sensors and print values to serial.
2021-08-21 Local version of ArduinoJson
2021-08-21 Output a JSON string of sensor data.
2021-08-22 Changed JSON capacity to make sure all data is serialized.
    Additionally added 1000ms delay to end of loop so the microcontroller is not always processing and writing to serial.
2021-09-04 added ArduinoJson to the cpp_props
2021-09-06 Completed functionality for parsing JSON. Then publishing it to the sensor reading topic
2021-09-07 Changed enums.py to constants.py. Added single spot mappings for device path names.
2021-09-07 Added start and end read times to sensor reads.
2021-10-31 Initial commit of basic webui framework
2021-11-03 Create new nodes for program, motion, and esp mock
    Started building message flow for new program and motion nodes
2021-11-04 Make message passing channels and sequence work
    Worked on logic in each of the nodes, fixed the multithreading for
    calling camera and sensor at same time
2021-11-22 Add Camera model which can generate ordered centroids based on settings
2021-11-22 Improved program flow
    * Revised program_executor to include image stitching
    * Fixed ESPMock and motion_executor to move in direct paths between
    waypoints
    * Added constants for database and image paths
    * updated SensorService to include program_run_id and waypoint_id
    * updated MotionService to use float instead of int
    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
2021-11-24 adding partial Camera class/Micasense class for camera_service
2021-11-26 adding picture and storage functionality to micasense class and camera mock
2021-11-26 commenting out text in camera_executor
2021-11-26 Add individual GCode processing and coordination
    * Create new topic for monitoring current activites
    * Create new service for sending individual gcodes to motion node
    * Add logic for handling overlapping movement requests
2021-11-30 minor edits, add subscriber to sensormock
2021-12-01 adding camera connection verifier
2021-12-01 changing parameter run_waypoint_id processing camera
2021-12-03 adding comments, testing functions below camera classes, fixing bug within directory making,tested without micasense and works
2021-12-03 Update README.md
    Adds link to sensor interpretation README
2021-12-11 add roslaunch, add query and reading for sensor parser, added mock for testing greenhouse message formatw
2022-01-09 update camera executor and db queries
    changed some commands to fix typos / syntax errors with the Micasense API (need to add a "database entry" function to add new captures to database
2022-01-09 Update camera_executor.py
    FOR SOME REASON the micasense API config selection says to configure the raw .tif format response you must submit a SET request with TIFF not TIF...
2022-01-16 Add Inventor files to main repo
    [032-0256-000_1.ipt, 0402_H040.ipt, 0402_H060.ipt, 041-0092-000_1.ipt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]
2022-01-16 update assembly with local references
    moved all assembly references to be localized to repo. Updated assembly with parts to reflect change
    [03_07_012_0_160_5.0003.iam, 03_07_012_0_160_5.iam, 03_07_012_0_160_5.stl, 03_07_012_0_160_5.stp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]
2022-01-18 update camera and status html files
2022-01-19 Update camera executor and compositor
2022-01-25 update buffer and ebox assembly
    [AddOn_Module.0007.iam, AddOn_Module.0008.iam, AddOn_Module.iam, Buffer.0017.iam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]
2022-01-27 add camera mount updates
    [Camera_Mount.0005.ipt, Camera_Mount.0011.ipt, Camera_Mount.0016.ipt, Camera_Mount.0022.ipt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]
2022-01-30 update camera mount
    [Camera_Mount.0022.ipt, Camera_Mount.0025.ipt, Camera_Mount.ipt, Camera_Mount.stl]
2022-01-30 Create Inventor Project and update Assembly references
    Created a base project within Inventor Files which will act as a reference point for all sub-assemblies (should not matter about root references).
    [1.iam, 10mm_Idle_Pulley_3M.0001.ipt, 10mm_Spacer.0001.ipt, 11-5512_.ipt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]
2022-01-31 update ebox with fasteners
    add fasters and subassemblies to Ebox
    [94180A333_Tapered Heat-Set Inserts for Plastic.STEP, 94180A353_Tapered Heat-Set Inserts for Plastic.STEP, 94180A361_Tapered Heat-Set Inserts for Plastic.STEP, 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]
2022-01-31 Quick update to Ebox
    [95783A051_Nylon 6 6 Male-Female Threaded Hex Standoff.ipt, 95783A057_Nylon 6 6 Male-Female Threaded Hex Standoff.ipt, 95783A069_Nylon 6 6 Male-Female Threaded 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]
2022-02-01 update PCBA files for manufacturing
    [BOM_PartType-Integrated Stepper Motor Driver.xlsx, Main.GBL, Main.GBO, Main.GBS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]
2022-02-02 add BOM
    [HyperRail_BOMv2.xlsx, RightAngle_Bracket_60mm.0004.ipt, RightAngle_Bracket_60mm.ipt]
2022-02-03 add new camera files
    [121-11-2-00-02(TripodAdapter).ipt, 121-11-22(FPGA-RJ45_C-Frontpl-18,1_ER-11,7).iam, 121-11-22(FPGA-RJ45_C-Frontpl-18,1_ER-11,7).stp, 121-11-22(FPGA-RJ45_C-Fron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]
2022-02-06 Add new launch files for new camera
2022-02-07 update camera files to use new camera properly
2022-02-07 Update camera files to use DFK machine vision camera
2022-02-08 add updated PCB files
    [BOM_PartType-ESP32 GRBL Controller.xlsx, Main.GBL, Main.GBO, Main.GBS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]
2022-02-10 add inventor files
    [121-11-22(FPGA-RJ45_C-Frontpl-18,1_ER-11,7).0001.iam, 121-11-22(FPGA-RJ45_C-Frontpl-18,1_ER-11,7).iam, Top_Rail_Full.0010.iam, Top_Rail_Full.iam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]
2022-02-15 update carriage with better x_plates
    [Carriage_Assembly.0069.iam, Carriage_Assembly.iam, Carriage_Horizontal_Spacer.0007.ipt, Carriage_Horizontal_Spacer.ipt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]
2022-02-22 Add BOMv3
    [20-2040_300mm.ipt, Bottom_Foot_Standoff.0022.ipt, Bottom_Foot_Standoff.ipt, Buffer.xlsx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]
2022-02-22 add rail assembly
    [Rail_AssemblyV2_0.0178.iam, Rail_AssemblyV2_0.xlsx, SDP_sdpsi_a_6r25mc1000.0002.ipt, SDP_sdpsi_a_6r25mc1000.0003.ipt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]
2022-02-25 add cable hook
    [Bottom_Foot.xlsx, CableHook.0001.ipt, CableHook.ipt, CableHook.stl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]
2022-03-01 update inventor files
    [Camera_Mount.0027.ipt, Camera_Mount.0029.ipt, Camera_Mount.ipt, Camera_Mount.stl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]
2022-03-04 add BOM3 changes and smaller CAD version
    [Carriage_Assembly.0082.iam, Carriage_Assembly.0083.iam, Carriage_Assembly.iam, HyperRail_BOM_OrderedChecklist.xlsx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]
2022-03-04 add ipn files for gifs
    [Rail_AssemblyV2_0_Assembled.ipn, Rail_AssemblyV2_0_tensioning.0001.ipn, Rail_AssemblyV2_0_tensioning.ipn]
2022-03-08 add bom and assembly updates
    [HyperRail_BOMv3.xlsx, Rail_AssemblyV2_0_tensioning.0001.ipn, Rail_AssemblyV2_0_tensioning.0002.ipn, Rail_AssemblyV2_0_tensioning.ipn]
2022-03-08 update full assembly
2022-03-17 add design data
    [032-0256-000_1.ipt, 0402_H040.ipt, 0402_H060.ipt, 041-0092-000_1.ipt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]
2022-04-04 Updated assemblies with small changes
    [ESP32GRBL_Mount.0001.iam, ESP32GRBL_Mount.iam, Jetson_Mount.0001.iam, Jetson_Mount.iam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]
2022-04-11 add admin material and supporting docs
    [Engineering Requirements.xlsx, JuniorDesign_Block1Checkoff.xlsx, JuniorDesign_Block2Checkoff.xlsx, JuniorDesign_SystemVerification (version 1).xlsb.xlsx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]
2022-05-15 update PCB files
    [1.iam, 1576890368.iam, 1576890496.iam, 1576890624.iam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]
2022-12-10 Added Code Flow Chart in Draw.io
2022-12-10 Add basic ESP32 Node
